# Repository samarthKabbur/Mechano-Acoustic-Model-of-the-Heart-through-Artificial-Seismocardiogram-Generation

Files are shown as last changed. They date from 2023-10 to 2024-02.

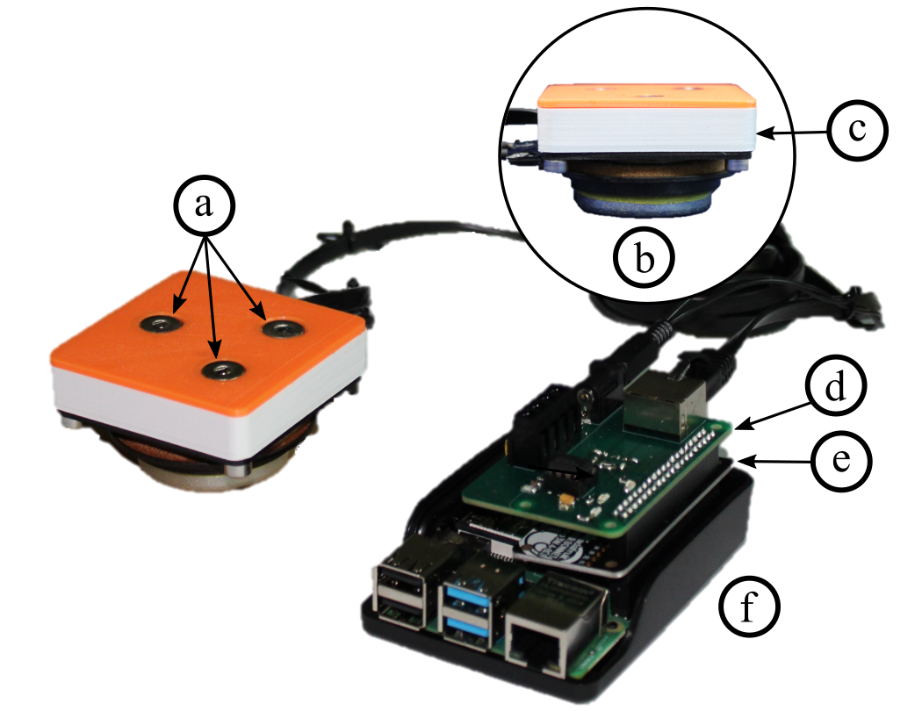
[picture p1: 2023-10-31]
SCG Generator/rPi Backups/Desktop/SyntheticSCG-Hardware-main/figures/figure1.png

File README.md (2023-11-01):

# Mechano-Acoustic-Model-of-the-Heart-through-Artificial-Seismocardiogram-Generation

URF Project Development Proposal for a Mechano Acoustic Model of the Heart through Artificial Seismocardiogram Generation and Cardiac Tissue Modeling
PI: Dr. Nanshu Lu, Mentor: Sarnab Bhattacarya, Researcher: Samarth Kabbur, University of Texas at Austin
Background and Statement of Objectives
1 			2			3		

Figure 1: Assorted imagery. 1. Heart with muscle damage and blocked artery. 2. SCG data collection flowchart. 3. Proposed artificial seismocardiogram generation system.
“Intelligence will transform our ability to monitor and detect heart disease,” says Dr. Peter Libby, a renowned cardiologist at Harvard-affiliated Brigham and Women's Hospital.1 His words encapsulate the ever-increasing importance of leveraging cutting-edge technologies to address one of the most prevalent and impactful health concerns affecting the public today – cardiac complications (Fig 1.1). 
At the forefront of cardiac monitoring is seismocardiography, or SCG, which allows us to measure the mechanical motion of the heart. SCG has shown remarkable promise in its utility, holding the potential to revolutionize the early detection and prediction of atrial fibrillation6, CAD7, and heart failure6,7, potentially years before they manifest clinically (Fig 1.2). While the promise of SCG is undeniable, the development of sensors capable of accurately measuring SCG and deriving meaningful physical characteristics of the heart from its signals has been hindered by challenges. Progress has been slow, and the cost of development has been prohibitive.2 In response to these limitations I aim to create a device that advances upon the capabilities of existing artificial SCG waveform generators.This device will have the ability to artificially generate a wide range of waveforms, enabling researchers to rigorously test their SCG sensors by placing them on top of artificial tissue. By doing so, we will establish an anatomically accurate mechano-acoustic model of the heart, enabling the development and testing of non-invasive devices under various simulated heart conditions (Fig 1.3). The implications of such a device are profound, as it can be employed broadly in research clinics and commercial testing, provided it receives the necessary approvals.
While existing SCG Generator Phantoms have demonstrated the ability to replicate SCG waveforms with up to 90% accuracy, there remain several unexplored avenues.3 This research seeks to answer important questions regarding the use of alternative transduction methods, such as piezoelectric, for SCG generation. Additionally, by introducing configurable noise and artifact simulation into the system, this study aims to enhance the utility of artificial SCG signal generation for algorithm testing.
The significance of this study will be underscored if the developed device consistently and accurately reproduces SCG waveforms recorded by gold standard SCG sensors in real human subjects. Furthermore, the incorporation of artificial tissue layers into the waveform generation process holds the potential to contribute to the creation of more realistic SCG waveforms, advancing the state of the art in this field.This research is expected to be of particular interest to seismocardiogram researchers and those involved in SCG sensor development, as it promises to accelerate the testing phase of their projects. Many within our laboratory share these research interests.
In conclusion, the objectives of this study are twofold: the primary objective is to assess if the inclusion of artificial tissue composed of PDMS and other biopolymers enhances the accuracy of artificial SCG waveforms, while the secondary objective seeks to explore the procedural combination of noise artifacts with SCG waveforms.  It addresses critical questions, introduces innovative approaches, and holds the promise of improving the reliability and accuracy of SCG sensor technology.
Proposed Research Plan
    1			2	                  3			   4

Figure 2: Prototype results of a speaker based SCG transduction/generation platform. 1. The 10.7cm x 10.7cm base plate and ADXL355 accelerometer 2. The hexagonal cross-structure and sandwich. 3. Side profile reveals the Visaton EX60-S electrodynamic exciter, printed support base, bottom cushion, and the top placement of direct SCG measurement 4. rPi 3B computational structure for interface with the exciter and accelerometer. The rPi hat is developed by Nikbakht et.al.
2.1 Build and validate a speaker based SCG transduction platform that allows for the vibrational playback of Heartsound.wav waveforms.
Under the guidance of my mentor and previous work on a SCG Generator Phantom (hardware and software) by Nikbakht et.al3 I have developed a mechano-acoustic foundation for the artificial generation of SCG waveforms, a critical component of our research methodology (Fig 2). This system has been structured to facilitate validation through external sensor measurements. The core of this setup features a carefully designed base plate characterized by dimensions and curvature tailored to minimize internal echoes (Fig 2.1). Positioned atop this base plate is an accelerometer, responsible for recording the SCG waveform (Fig 2.1). To bolster mechanical coupling and optimize vibration transmission, a hexagonal cross structure is sandwiched within (Fig 2.2). The uppermost layer comprises a thin, rigid printed plastic roof plate, serving as the platform for the placement of the external SCG measurement device (Fig 2.3). Connecting these elements is a Raspberry Pi housing Python code that not only transmits the SCG waveform for playback but also collects internal vibration data from the accelerometer (Fig 2.4).
This endeavor benefits from the existence of more advanced software, as seen in the work by Nikbakht et.al. This software encompasses a comprehensive suite of features, including a feedback transfer function for waveform calibration against noise, error handling mechanisms, terminal-based inputs for precise control over playback, and it performs well on my mechanical model. In my research, I intend to draw inspiration from and further develop this existing codebase to refine and optimize my own system for SCG signal generation and validation.
	2.2 Build and study the effect of anatomically correct cardiac tissue layers composed of eco-polydimethylsiloxane and other bio-polymers on the generation of accurate artificial seismocardiogram waveforms.
SCG sensors do not sit directly on top of the heart, rather they read signals that need to travel through many layers of bone and tissue, including the myocardium, peritoneum, sternum, etc.2 Using our available eco-PDMS and other biopolymers as necessary, I will create layers of variable thickness, density, and composition to create a low-level structure mimicking the anatomical layers of the heart. The layers will rest on the top surface of the existing SCG Generator. Experimental testing will determine if the biostructure allows for a generation of a more accurate SCG signal, compared to a barebones platform. The testing will include varying the mechanical coupling between layers, changing the weight of the sensor itself, and varying tissue density all as independent variables.
	2.3 Create an algorithm that can incorporate noise artifacts (walking, running, stomach palpitations, small impulse) into a clean SCG signal.
Available SCG databases are limited, and sometimes a researcher may want to test their sensors on a unique signal that isn’t available to us. For example, the topic of research may deal with creating an e-tattoo that can detect SCG features while the patient is walking, running, etc. Citation no. 2 also describes this problem as a gap in existing literature. I will create a novel program that can combine noise artifacts generated by walking, running, hiking, swimming, etc. with a ‘clean’ SCG signal, in order to simulate a ‘dirty’ signal. Such a signal would then be played in the SCG Generator for testing purposes, allowing the researcher to test their device on a large variety of signals, all on a small in-house machine, allowing them to minimize expensive human trials.
Project Schedule and Milestones
Task
Subtask
Y1
Q1
Q2
Q3
Q4

1
Optimize and groove mechanical structure 

Mitigate external noise

2
Methodize variable density PDMS production

Manufacture tissue layers

Validate signal accuracy

3
Accumulate noisy and clean datasets

Procedural generation of noisy signal

Validate signal accuracy to ground truth

Review of Literature
A seminal external study that significantly informs the present research is the work titled "A Synthetic Seismocardiogram and Electrocardiogram Generator Phantom," authored by Mohammad Nikbakht et. al. This study introduced a portable and innovative system designed to synthetically generate SCG and electrocardiogram (ECG) signals. The researchers developed a Raspberry Pi-based system capable of replicating input SCG and ECG waveforms as physical acceleration and voltage outputs. For SCG generation, an off-the-shelf exciter speaker was employed as a mechanical transducer, and its transfer function was meticulously calibrated to ensure accurate replication of SCG waveforms. The system's performance was rigorously validated using human SCG and ECG data, achieving a remarkable >90% correlation between input and output signals in both time and frequency domains. Importantly, amplitude errors were maintained within clinically acceptable ranges, allowing the system to produce realistic waveforms with amplitudes corresponding to critical cardiac features. This innovation enables safe data collection in environments unsafe for human participants and provides a valuable source of ground truth signals.
While the aforementioned study represents a significant advancement in SCG signal generation, there remain opportunities for further development and improvement. First, expanding the validation process to encompass more diverse SCG morphologies, as well as various cardiac conditions, will enhance the applicability and reliability of the synthetic signal generator. The addition of noise artifacts associated with walking, running, and other forms of human mobility to the input waveform can help synthesize the effect of real world continuous processes on the heart. Finally, the proposed research seeks to build upon this foundation by creating a device that not only generates SCG signals but also incorporates artificial tissue layers to model the complex physiological nuances of the human body.
Budget
Raspberry Pi 4b+ KIT: Faster processor unlocks real time SCG processing and computationally intensive Python packages: $186
PDMS and Crosslinker: Biopolymer to simulate tissue layers: $175
Visaton 60s Electrodynamic Actuator x2: Generates the main SCG signal: $160
PAD Ex 60s x4: $120 x2: Adheres generator to surface, minimizes noise: $20
Piezoelectric Actuator: To study other methods of SCG generation: $12
Foam Padding: To pad external connections to minimize noise and internal vibration: $5
Polylactic Acid Filament: 3D printer material for foundation fabrication: $19
Ninjaflex Polyurethane Filament: 3D printer material for flexible plastics $28
Florida Biomedical Society 2024 Conference. (Coronado Springs, Florida, Feb 8-11, 8:30-10pm daily session time). The FBSS contains 48 hours of education sessions on topics relating to biomechanics. Researcher has identified these learning opportunities as valuable for the progress of his project, and has identified attending individuals, companies, and products highly relevant to this research and my career goals: $189 Registration Fee + $144 Hotel Fee. The researcher agrees to cover all extra conference related fees to guarantee attendance. (https://www.cmia.org/events/florida-biomedical-society-2024-symposium/)
Total: $938
The materials in the itemized budget are essential to the design and production of the proposal and validation study. While basic lab materials and electronic elements are available through courtesy of the PI, URF funding will expedite my research progress. It will also allow for stronger validation testing, robust manufacturing of the model, and quality materials.
References Cited
1.	Can a smart watch diagnose a heart attack? Harvard Health https://www.health.harvard.edu/heart-health/can-a-smart-watch-diagnose-a-heart-attack.
2.	Taebi, A., Solar, B. E., Bomar, A. J., Sandler, R. H. & Mansy, H. A. Recent Advances in Seismocardiography. Vibration 2, 64–86 (2019). doi: 10.3390/vibration2010005.
3.	A Synthetic Seismocardiogram and Electrocardiogram Generator Phantom. doi:10.1109/SENSORS52175.2022.9967101 
4.	Blocked Artery https://www.flickr.com/photos/nihgov/33328945325.
5.	Heart beat detection algorithm flowchart. https://www.researchgate.net/figure/Heart-beat-detection-algorithm-flowchart_fig3_33661771
6. M. Pankaala et al., “Detection of atrial fibrillation with seismocardiography,” doi: 10.1109/EMBC.2016.7591695.
7. I. Korzeniowska‐Kubacka, “Usefulness of Seismocardiography,” doi: 10.1111/j.1542-474X.2005.00547.x.

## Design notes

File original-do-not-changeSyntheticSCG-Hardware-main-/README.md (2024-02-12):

# Synthetic ECG SCG Generator Hardware

The seismocardiogram (SCG) is a measure of chest wall vibrations resulting from the heartbeat. The SCG is typically
recorded using a low-noise accelerometer placed on the mid-sternum and contains features related to cardiovascular
activity such as aortic valve opening (AO) and aortic closing (AC). These features can support assessment of cardiovascular health and have been used in conjunction with other physiological signals to monitor key health parameters such as blood volume status and intracardiac filling pressures.

Electrocardiogram (ECG) signal reflects the electrical activity of the heart observed from the strategic points of the human body and represented by quasi-periodic voltage signal.
<!-- 
These signals fiducial points correspond to characteristic events in the cardiac cycle. For the SCG, the labels correspond to the physiological event they are believed to represent: MC, mitral valve closure; IVC, isovolumetric contraction; AO, aortic valve opening; RE, rapid ejection; AC, aortic valve closure; MO, mitral valve open- ing; and RF, rapid filling. -->

<!-- However, SCG signals are small signal, and they can get distorted easily by motion artifacts. Therefore exploring denoising methods is of great importance for SCG signals. Clearing out the noise enables extraction of physiologically relevant information from SCG. To study denoising methods, we need to collect SCG signals in noisy environments, but it is unsafe to use human subjects for such data collection in some high motion environments (medical transport helicopters). To address this, here we designed a phantom that can generate SCG and ECG signals synthetically. This enables us to collect data in those noisy environmnets without human subject involvement.
 -->
In this work, we introduce a portable USB-C powered Raspberry Pi-based system that can replicate any SCG and ECG signal inputs with minimal error in forms of acceleration and voltage. The SCG signals are generated using an off the shelf exciter speaker, and the ECG signals are generated using a voltage amplifier through 3 conductive pads. The generated signals can be recorded using the same wearable devices that are used to measure human SCG and ECG signals. Thus, this system can be used as a safer, more convenient alternative to human participants in high external vibration environments for testing and validating
classification/regression tasks and noise reduction algorithms.

## The Hardware 

he system proposed in this work consists of an actuator unit and a processing unit. The actuator unit, which generates SCG and ECG signals. 

<p align="center">
Image of The ECG/SCG Patch
</p>

<!-- <img src="https://github.com/mohnikbakht/Synthetic_ECG_SCG_Generator_Demo/blob/main/Images/Actuator2.png" alt="Image of The ECG/SCG Patch" width="300"/> -->

The system designed here offers two user-controlled modes of operation: (1) calibration, which re-estimates the transfer function of the exciter speaker with the added load on the platform (wearable sensors) , and (2) signal generation, which generates the ECG and SCG sequences.

A block diagram of the system operation:
<p align="center">
 Image of The ECG/SCG Patch
</p>

### Commands

1) Calibration mode: Calibrate the system (in a new environment):

calculate the transfer function of the actuator using a sine sweep and use it to calibrate the SCG beats to be ready for generation
 
```console
python3 SCG_Generator.py tf_estimate desktop
python3 SCG_Generator.py calibrate seq_synth desktop (or any file name [without .pkl])
```
<!-- 
<img src="https://github.com/mohnikbakht/Synthetic_ECG_SCG_Generator_Demo/blob/main/Images/calibrate_1.png" alt="Image of The ECG/SCG Patch" width="400"/> -->

2) Generation mode: Generate SCG waveforms:

generate SCG and ECG signals using the calibrated beats stored in the previous step

```console
python3 SCG_Generator.py generate seq_synth_calibrated desktop (or any file name you stored the calibrated signals [without .pkl])
```

<!-- <img src="https://github.com/mohnikbakht/Synthetic_ECG_SCG_Generator_Demo/blob/main/Images/generate_1.png" alt="Image of The ECG/SCG Patch" width="400"/> -->

## Use

Depending on the type of the connection to the RPi, there are 2 options:
1) If a display is connected to the RPi (or have X11 forwarding enabled), the plots will be shown in separate windows. Use this command (this mode is default):
```console
python3 SCG_generate.py generate signal_sample_calibrated desktop
```
2) If communication is through a terminal only, the plots will be plotted in the terminal (lower quality). Use this command:
```console
python3 SCG_generate.py generate signal_sample_calibrated terminal
```
## Output Recording Samples

A sample of the generator-output SCG and ECG compared to the ECG and SCG inputs:

<p align="center">
Image of The ECG/SCG Patch
</p>

Bland-Altman plots of error between the measured generator-output and the real human signal input based on the amplitude of the most prominent
feature of the beats after heartbeat segmentation for (a) SCG, and (b) ECG signals. 

<p align="center">
Image of The ECG/SCG Patch
</p>

<!-- Zoomed in:

<img src="https://github.com/mohnikbakht/Synthetic_ECG_SCG_Generator_Demo/blob/main/Images/sample_2.png" alt="Image of The ECG/SCG Patch" width="600"/>

 -->

## Reference

Please cite this paper:

M. Nikbakht, D. J. Lin, A. H. Gazi, and O. T. Inan, “A synthetic
seismocardiogram and electrocardiogram generator phantom,” in 2022
IEEE Sensors, in press.

BibTeX format: 

@inproceedings{nikbakht2022synthetic,
title={A Synthetic Seismocardiogram and Electrocardiogram Generator Phantom},
author={Nikbakht, Mohammad, and Lin, David J., and Gazi, Asim H., and Inan, Omer T.},
note={in press},
booktitle={2022 IEEE Sensors},
% pages={Accepted},
% year={2022},
% organization={IEEE}
}

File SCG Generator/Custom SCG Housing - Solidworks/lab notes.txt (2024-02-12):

propyl alchohol destroys polycarbonate plastics and filmms

methyl alchohol destroys ABS plastics and films : is polycarbonate film elastic

sent two to pig, and one broke. pig study was good data, then went bad. pig people gave singular ppg waveform so it was useless bc spO2 was needed.
btw in the interest of good communication, here's everything im working on and an approximate time frame:

projects:vibration table using raspberry pi
	
	 soluble plastic film for easier recycling of chest e-tattoo.

to learn:

	raspberry pi interface
	C code
	python signal processing MIT BSC lab
	ML algorithms
	Embedded systems
	LHR application
	IEEE robotics application
	matlab
	fast fourier transform
	signal filtering and the different types of filter implementation like Butterworth, chevychev etc. And how to filter signals based 	on set frequencies

to talk to:
	
	talk to tiande for the ecg tattoo codebase. he comes in around 4:30pm.
	talk to jishnu for sneaking into embedded systems lab
	-> the chemicals lady in the soft bioelectronics lab for getting plastics, alchohols, and training on the fume hood.

meetings:
	team meeting - tuesday at 3pm
	group meeting - friday at 9am

to organize: 
	CAD/Eagle model of chest e-tattoo
	calendar
	github codebase
	research/notes of raspberry pi 

possible projects: 
	fully flexible ears
	higher wire density
	SpO2 on the chest
	moving from coin cell to lion battery 
	trimodal: PPG, SCG, ECG
	bimodal: SCG, ECG
	dual device: SCG+SCG, ECG

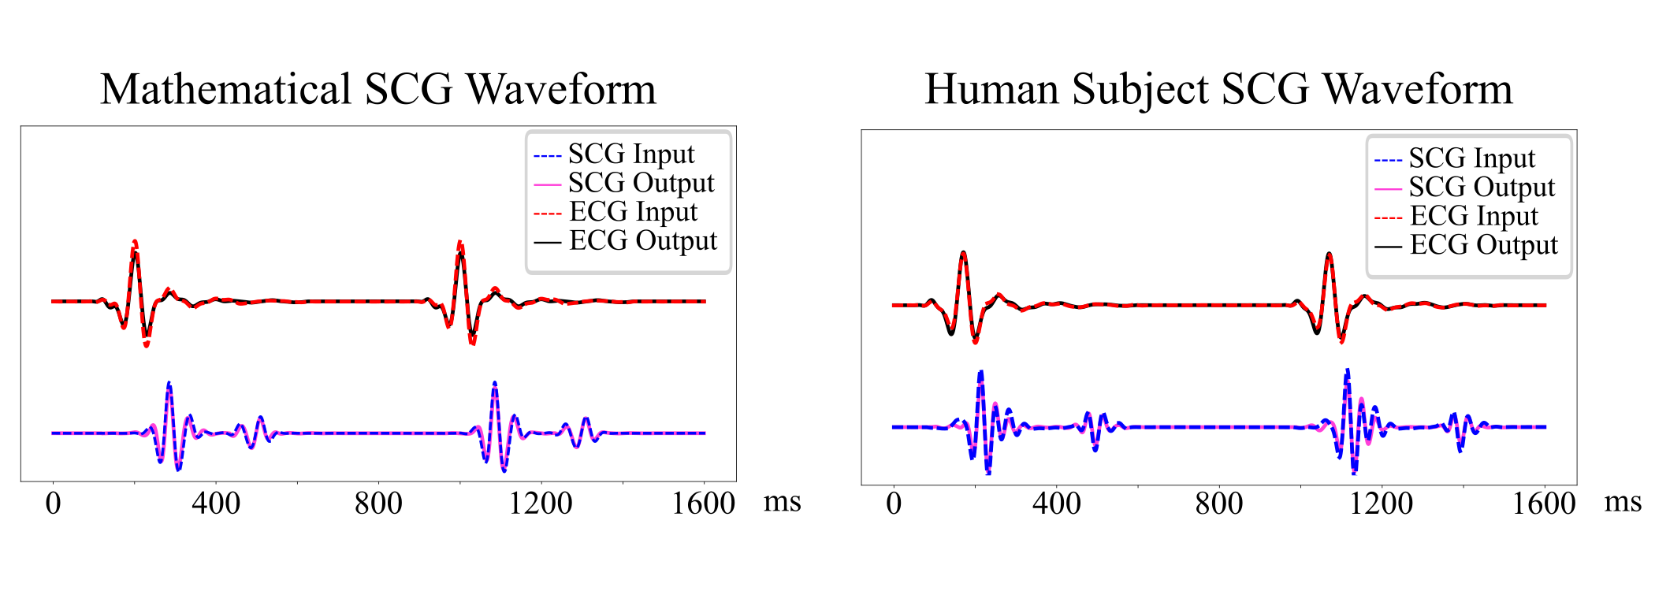
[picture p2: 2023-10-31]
SCG Generator/rPi Backups/Desktop/SyntheticSCG-Hardware-main/figures/figure3.png

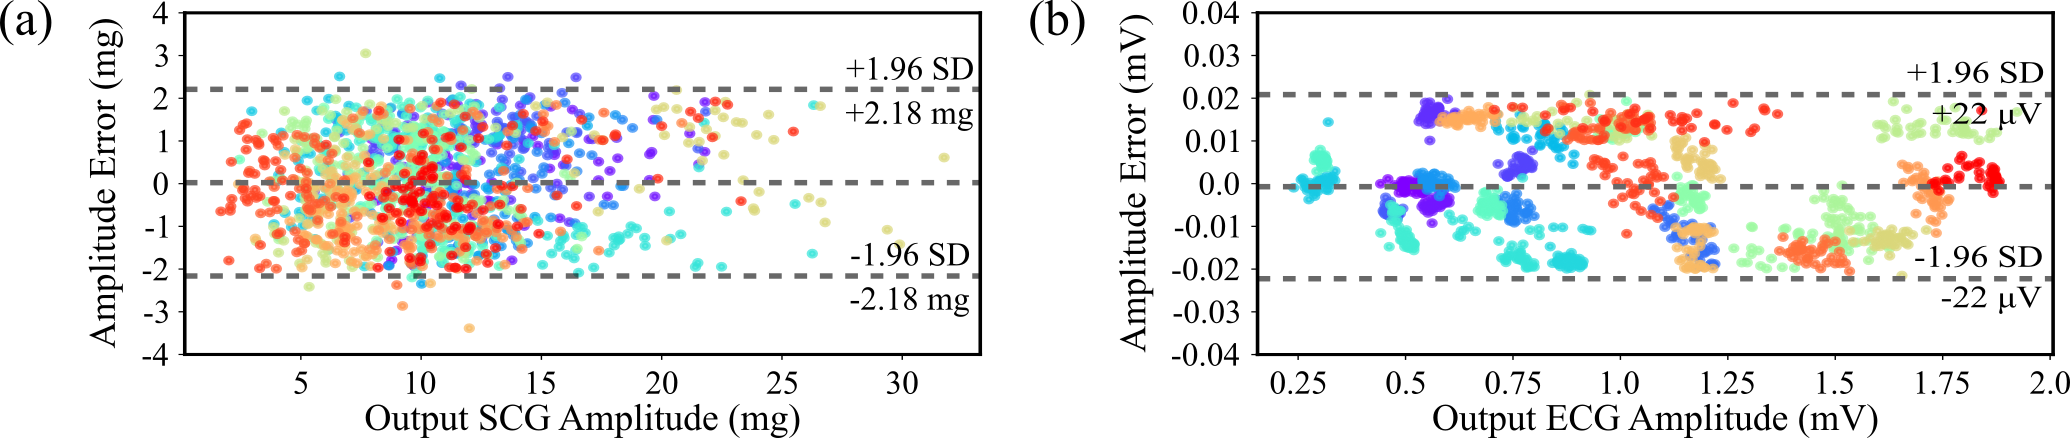
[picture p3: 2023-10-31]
SCG Generator/rPi Backups/Desktop/SyntheticSCG-Hardware-main/figures/bland-altman.png

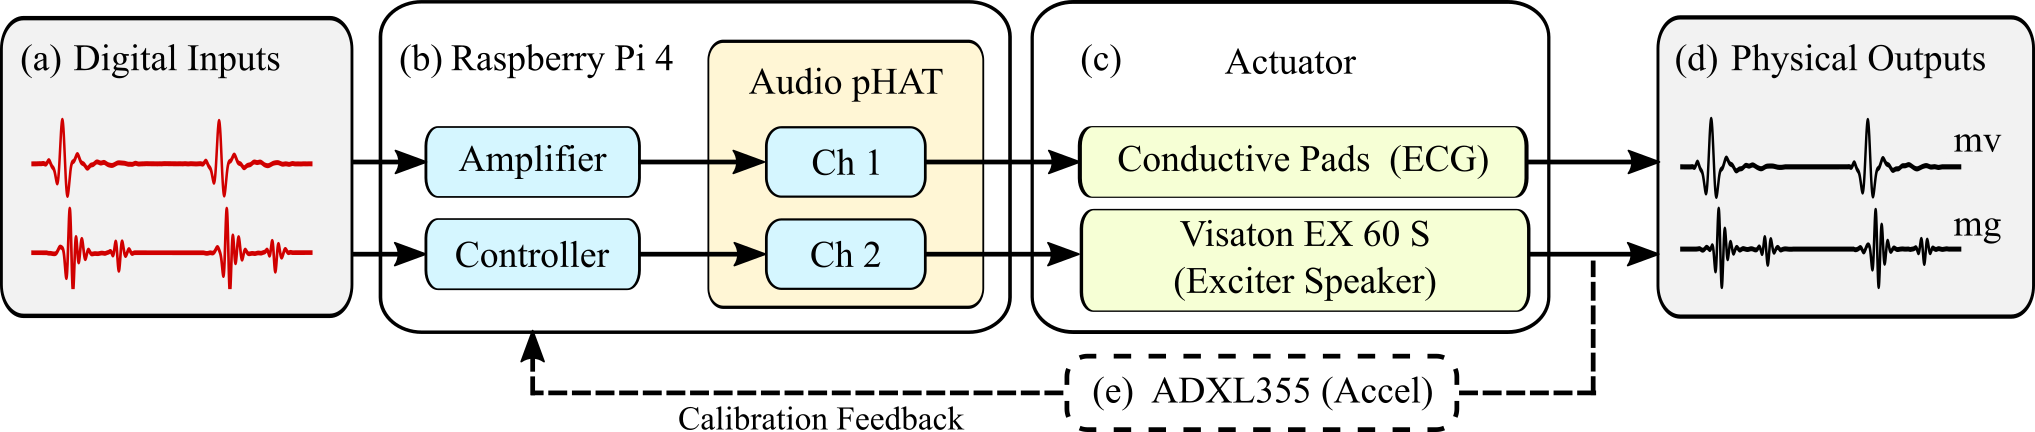
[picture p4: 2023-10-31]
SCG Generator/rPi Backups/Desktop/SyntheticSCG-Hardware-main/figures/figure2.png

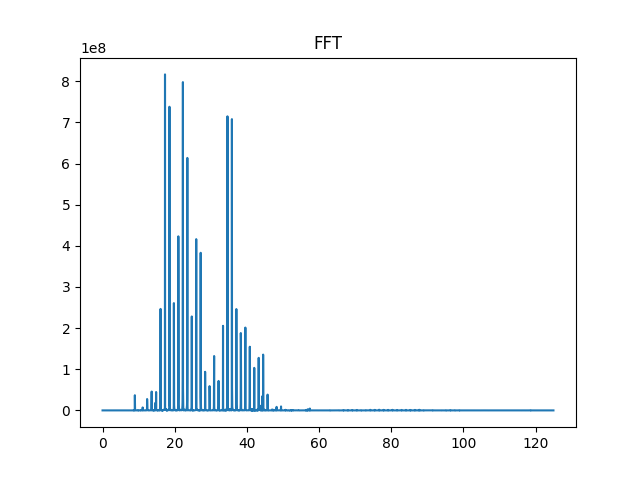
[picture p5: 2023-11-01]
oldbase-RPi code/Trials/Trial 2/fft.png

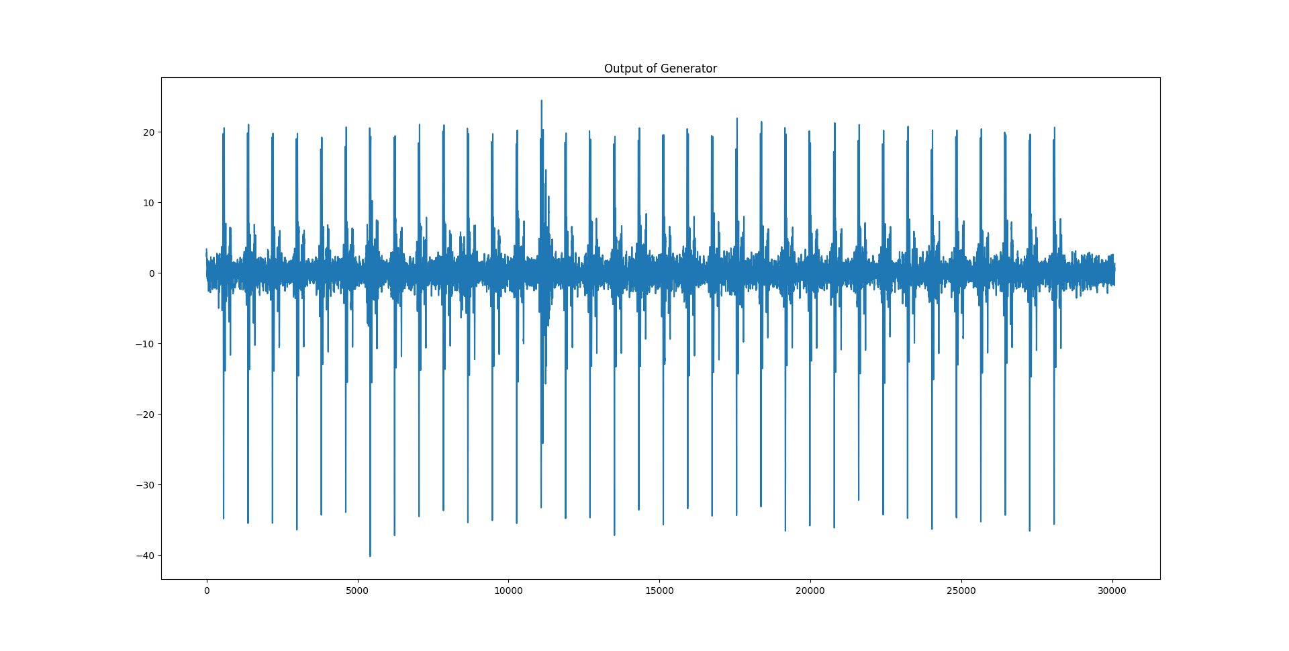
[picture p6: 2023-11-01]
oldbase-RPi code/Trials/Trial 1/Figure_1.png

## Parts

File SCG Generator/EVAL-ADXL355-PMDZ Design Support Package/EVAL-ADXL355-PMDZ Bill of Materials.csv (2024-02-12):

TITLE: Bill of Materials
BOM NO: 05_043217-b.csv
DATE: 01/24/2017
DESIGN: 02_043217b_top
TEMPLATE: Z:\allegro\v166_site\cdssetup\template.bom
CALLOUT:
ITEM# | Qty | WW_PN | DESCRIPTION | VALUE | JEDEC_TYPE | TOL | VOLTAGE | WATTAGE | LOCATION | MFG | MFG_PN | HLM_STATUS | STOCKROOM_WL | STOCKROOM_GT | STOCKROOM_LK | STOCKROOM_GBO | STOCKROOM_NSH | CUSTOM_PART | DNI
1 | 1 | 08_043217b | PCB | ? | ? | ? | ? | ? | ? | Analog Devices Supplied | 08_043217b | N/A | ? | ? | ? | ? | ? | ? | ?
2 | 4 | E022221 | CAP CER MULTILAYER X7R | 0.1uF | C0603 | 5 | 16V | N/A | C1,C2,C4,C5 | KEMET | C0603C104J4RACTU | REL | N/A | N/A | N/A | N/A | N/A | ? | ?
3 | 2 | E020723 | CAP CER X5R | 10uF | C0603 | 10 | 10V | N/A | C3,C6 | TDK | C1608X5R1A106K080AC | REL | N/A | N/A | N/A | N/A | N/A | ? | ?
4 | 1 | E015984 | IND CHIP FERRITE BEAD | 330OHM | L0603 | 25 | N/A | N/A | E1 | MURATA MANUFACTURING | BLM18SG331TN1D | REL | N/A | N/A | N/A | N/A | 7005146 | ? | ?
5 | 1 | E002359 | INDUCTOR FERRITE BD | 39OHM | L0805 | N/A | N/A | N/A | E2 | PANASONIC | EXC-ML20A390U | REL | A048-0002-010 | N/A | N/A | 1424_CAB3 | 7005175 | ? | ?
6 | 1 | E018495 | CONN-PCB HDR RA CUSTOMIZED PIN NUMBERING -PMOD | TSW-106-25-F-D-RA | CNHDRRA2X6H240 | N/A | N/A | N/A | P1 | SAMTEC INC | TSW-106-25-F-D-RA | NON-PREF | N/A | N/A | N/A | N/A | N/A | ? | ?
7 | 1 | E025232 | RES THICK FILM CHIP JUMPER, GENERAL PURPOSE | 0 | R0402 | N/A | N/A | 1/16W | R1 | YAGEO | RC0402JR-070RL | REL | N/A | N/A | N/A | N/A | 7008627 | ? | ?
8 | 1 | E024010 | IC-ADI LOW NOISE, HIGH STABILITY, LOW POWER 3AXIS ACCELEROMETER, PRELIM | ADXL355BEZ | LCC14_A | N/A | N/A | ? | U1 | ADI | ADXL355BEZ | RWC | N/A | N/A | N/A | N/A | N/A | ? | ?
The following components are part of the PCB or are NOT to be installed
ITEM# | Qty | WW_PN | DESCRIPTION | VALUE | JEDEC_TYPE | TOL | VOLTAGE | WATTAGE | LOCATION | MFG | MFG_PN | HLM_STATUS | STOCKROOM_WL | STOCKROOM_GT | STOCKROOM_LK | STOCKROOM_GBO | STOCKROOM_NSH | CUSTOM_PART | DNI

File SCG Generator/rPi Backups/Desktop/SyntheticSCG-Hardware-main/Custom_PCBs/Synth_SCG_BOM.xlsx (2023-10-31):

Part | Value | Device | Package | DigiKey Part Number
C1 | 220pF | C-US_CHIP-1206(3216-METRIC) | CAPC3216X135
C2 | 80nF | C-US_CHIP-0805(2012-METRIC) | CAPC2012X110
C3 | 220pF | C-US_CHIP-1206(3216-METRIC) | CAPC3216X135
C4 | 100nF | C-US_CHIP-0603(1608-METRIC) | CAPC1608X85
C5 | 80nF | C-US_CHIP-0805(2012-METRIC) | CAPC2012X110
C6 | 10uF | C_TANTALUM-1206(3216-METRIC) | CAPM3216X180
J1 | 1734795-1 | 1734795-1 | TE_1734795-1 | A121573-ND
J2 | PJ-035DH | PJ-035DH | CUI_PJ-035DH | CP-017DH-ND
LED1 |  | LEDCHIPLED_1206 | CHIPLED_1206
LED2 |  | LEDCHIPLED_1206 | CHIPLED_1206
LED3 |  | LEDCHIPLED_1206 | CHIPLED_1206
R1 | 10k | R-US_R0603 | R0603
R2 | 10k | R-US_R0603 | R0603
R3 | 0 | R-US_R0603 | R0603
R4 | 0 | R-US_R0603 | R0603
R5 | 4.7k | R-US_R0603 | R0603
R6 | 100R | R-US_R0603 | R0603
R7 | 100R | R-US_R0603 | R0603
R8 | NC | R-US_R0603 | R0603
R9 | 10 | R-US_R0603 | R0603
R10 | 100k | R-US_R0603 | R0603
R11 | 10k | R-US_R0603 | R0603
R12 | 100k | R-US_R0603 | R0603
R13 | NC | R-US_R0603 | R0603
RPI1 | RASPBERRYPI_BPLUS_BONNETNODIM | I2S 3W STEREO SPEAKER AMP BONNET | I2S 3W STEREO SPEAKER AMP BONNET | 1528-1819-ND
U$1 | TLV4112 | TLV4112 | DIP794W45P254L959H508Q8 | 296-10719-5-ND
U$2 | 2828XX-4282837-4 | 2828XX-4282837-4 | TERMBLK_508-4N | 281-1437-ND
 | Extra parts (digikey): |  | count
 | 2x20 Socket Riser Header for Rpi | 1528-2831-ND | 2
 | RPI female header | 1528-1785-ND | 2
 | RPi connector | 1568-1675-ND | 2
 | RPi stacking header | 1528-1385-ND
 | 12 Position Header Connector 0.100" (2.54mm) Through Hole, Right Angle | S5559-ND | 2
 | DC plug 3.5 | EP505B-ND | 2
 | Terminal blocks | ED2611-ND | 2
 | Terminal blocks | A97986-ND | 2
 | Dip socket | ED3044-5-ND | 2
 | Raspberry Pi 4 8GB | 2648-RASPBERRYPI4MODELB8G-ND | 1
 | ADXL355 eval board | 505-EVAL-ADXL355-PMDZ-ND | 1
 | ECG electrode pads | 1568-1803-ND | 2
 | Visaton EX 60 S Exciter Speaker | 2056-EX60S-8OHM-ND
 | screw and bolt 4mm
 | super glue + electric tape
 | Extra parts (Amazon):
 | Ethernet cable | https://www.amazon.com/Ethernet-Cable-1000Mbps-Universal-Computer/dp/B07H25B2S7
 | micro-SD card 32GB or 64GB

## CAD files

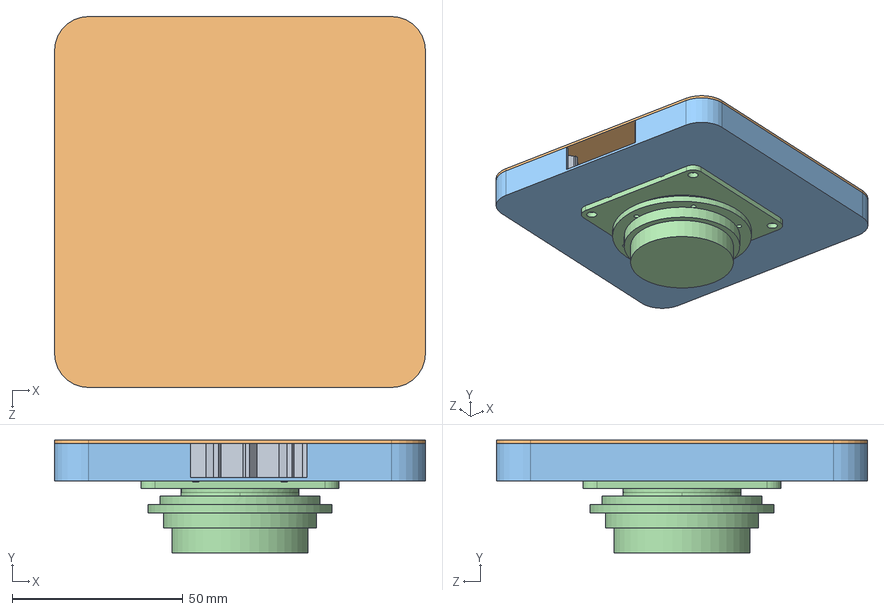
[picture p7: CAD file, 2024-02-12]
SCG Generator/Custom SCG Housing - Solidworks/speaker and attachment assembly.SLDASM
108.8 x 33.1 x 108.8 mm
visaton ex 60 s
attachment
lid
honeycomb

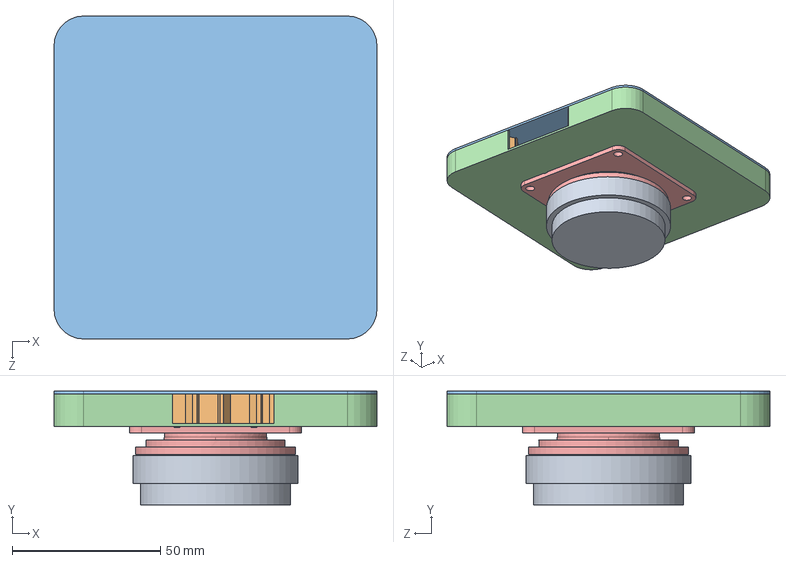
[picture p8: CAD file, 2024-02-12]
SCG Generator/Custom SCG Housing - Solidworks/speaker and attachment with BAE.SLDASM
108.8 x 38.4 x 108.8 mm
visaton ex 60 s
attachment
lid
honeycomb
visaton ex 60 s BASE

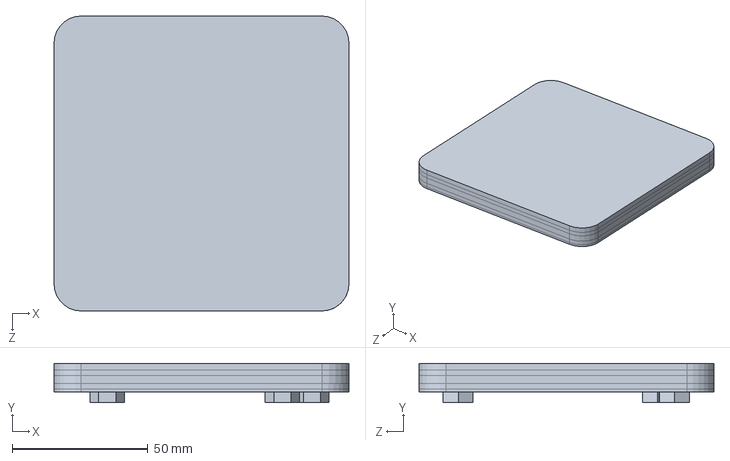
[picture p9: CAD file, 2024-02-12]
SCG Generator/Custom SCG Housing - Solidworks/lid_with_tissue_layers.SLDPRT
108.8 x 14.5 x 108.8 mm

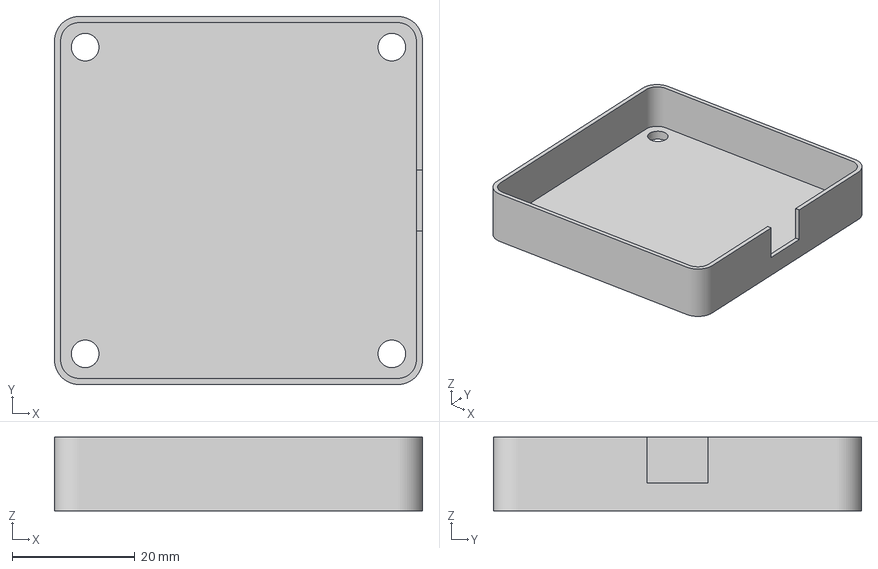
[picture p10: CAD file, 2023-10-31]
SCG Generator/rPi Backups/Desktop/SyntheticSCG-Hardware-main/Actuator_Housing_CAD_designs/Body.3mf
60.0 x 60.0 x 12.0 mm

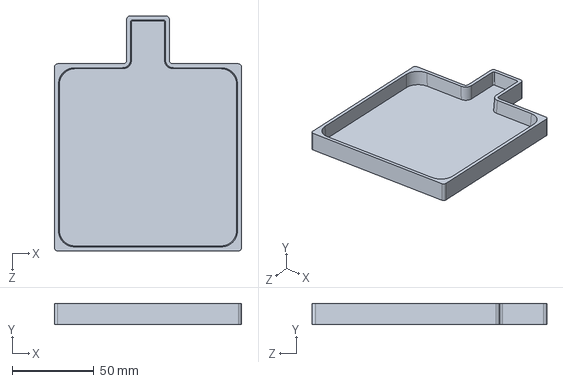
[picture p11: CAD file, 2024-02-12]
SCG Generator/Tissue Molds/mold1withlip.SLDPRT
114.8 x 13.0 x 144.1 mm

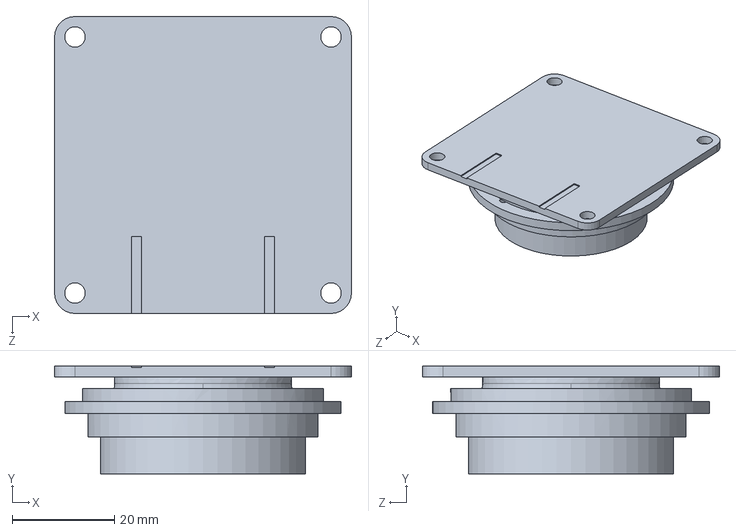
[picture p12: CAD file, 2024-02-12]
SCG Generator/Custom SCG Housing - Solidworks/visaton ex 60 s.SLDPRT
58.0 x 21.1 x 58.0 mm

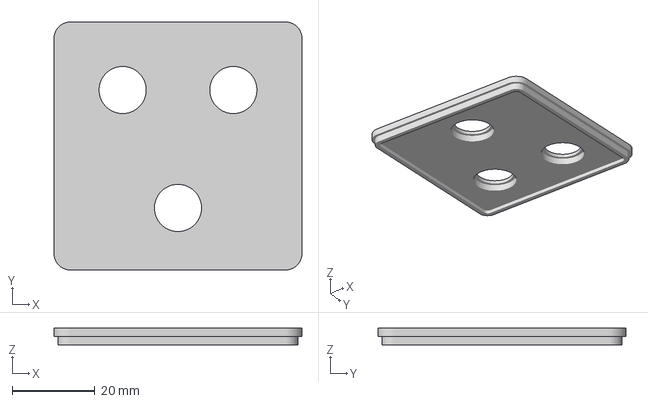
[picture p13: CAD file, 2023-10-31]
SCG Generator/rPi Backups/Desktop/SyntheticSCG-Hardware-main/Actuator_Housing_CAD_designs/Lid.3mf
60.0 x 60.0 x 4.00 mm

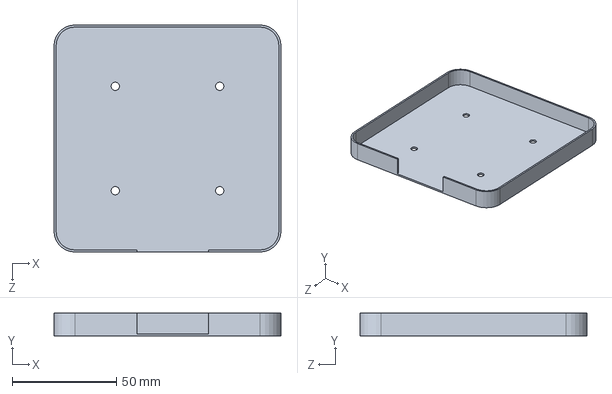
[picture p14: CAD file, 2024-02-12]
SCG Generator/Custom SCG Housing - Solidworks/attachment.SLDPRT
108.8 x 11.0 x 108.8 mm

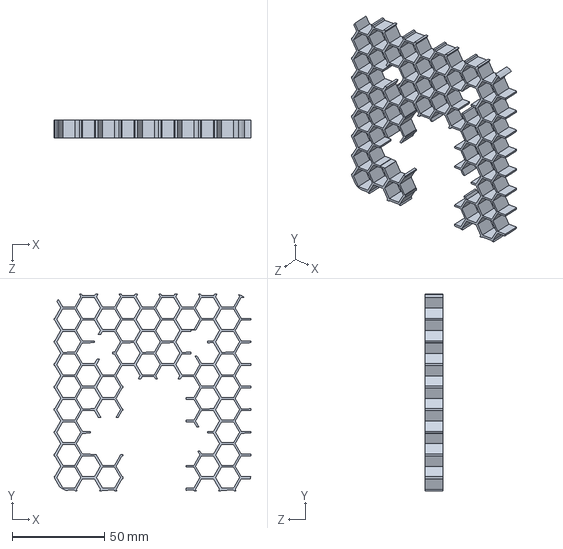
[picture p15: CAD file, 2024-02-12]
SCG Generator/Custom SCG Housing - Solidworks/honeycomb.SLDPRT
106.8 x 106.8 x 10.0 mm

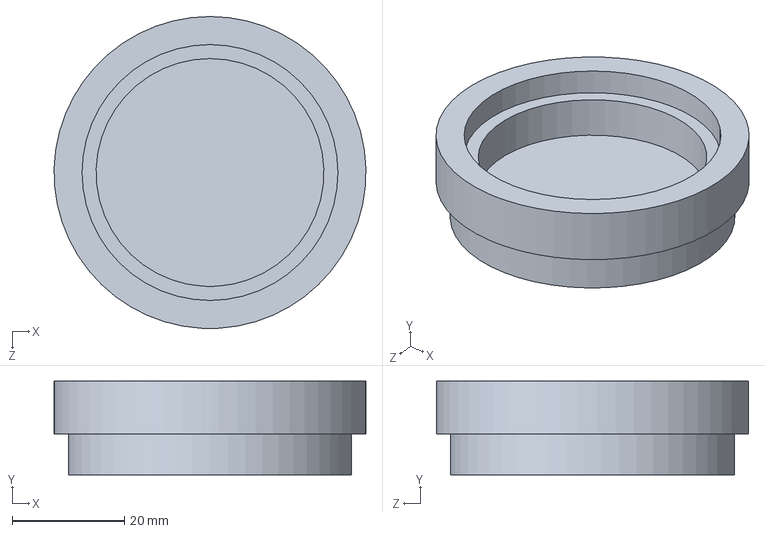
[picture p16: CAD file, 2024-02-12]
SCG Generator/Custom SCG Housing - Solidworks/visaton ex 60 s BASE.SLDPRT
55.6 x 16.7 x 55.6 mm

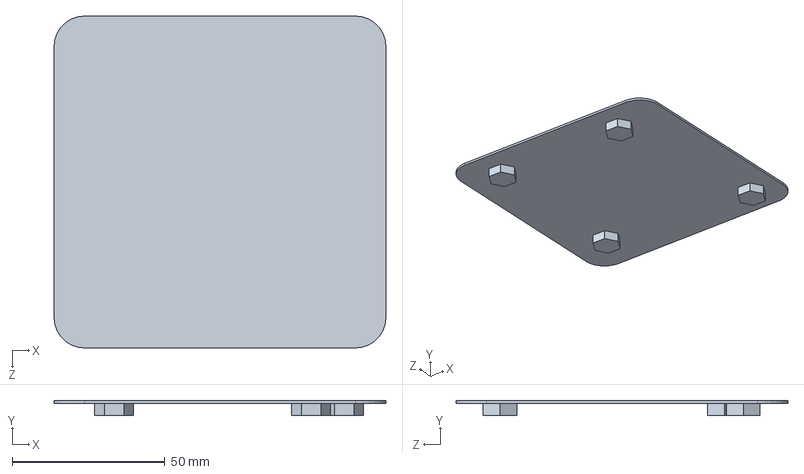
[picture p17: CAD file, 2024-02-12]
SCG Generator/Custom SCG Housing - Solidworks/lid.SLDPRT
108.8 x 5.00 x 108.8 mm

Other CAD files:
SCG Generator/rPi Backups/Desktop/SyntheticSCG-Hardware-main/Actuator_Housing_CAD_designs/Synthetic_SCG_Actuator_Housing.f3d
SCG Generator/rPi Backups/old transfer/Desktop/SyntheticSCG-Hardware-main/Actuator_Housing_CAD_designs/Synthetic_SCG_Actuator_Housing.f3d

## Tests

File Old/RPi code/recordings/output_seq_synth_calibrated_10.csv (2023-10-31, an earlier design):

-1.813951737450452129e-01
1.285004826254976251e+00
7.858048262548891216e-01
6.220048262549653373e-01
-4.879517374502029270e-02
6.454048262548894854e-01
9.496048262549265928e-01
3.568048262549154970e-01
2.710048262549662468e-01
4.036048262548774801e-01
4.738048262548772982e-01
6.142048262548769344e-01
1.316204826254875115e+00
9.160482625497934350e-02
-6.415951737450313885e-01
-5.479951737451074223e-01
4.480482625490367354e-02
-2.359951737450955989e-01
1.051004826254938962e+00
1.004204826254976979e+00
1.097804826254900945e+00
3.256048262549029459e-01
7.600482625491622457e-02
6.040482625496679248e-02
-6.415951737450313885e-01
-1.671195173745104512e+00
-1.070595173745118700e+00
5.206048262549529682e-01
2.751404826254884028e+00
4.701404826254929503e+00
4.795004826254967156e+00
1.948004826254873478e+00
7.600482625491622457e-02
-1.267951737451085137e-01
-8.521951737450308428e-01
9.184048262549140418e-01
5.596048262549402352e-01
2.236604826254961154e+00
1.940204826254898762e+00
3.022048262549787978e-01
-5.167951737450948713e-01
-2.047951737450830478e-01
1.696048262549538777e-01
6.532048262549778883e-01
4.738048262548772982e-01
-1.891951737450199289e-01
-7.819951737450310247e-01
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

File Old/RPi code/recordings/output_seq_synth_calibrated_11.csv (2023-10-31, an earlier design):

-2.439353378378427806e+00
-4.269533783783572289e-01
1.328046621621638224e+00
2.381046621621635495e+00
3.140466216216282191e-01
-1.191353378378380512e+00
-1.916753378378416528e+00
-1.557953378378442721e+00
-1.300553378378367597e+00
-6.531533783784198022e-01
-4.475337837834558741e-02
1.086246621621626218e+00
2.576046621621571830e+00
2.115846621621585655e+00
1.694646621621586746e+00
2.438466216216284010e-01
-9.885533783783557737e-01
-6.815337837838342239e-02
9.848466216216138491e-01
9.224466216215887471e-01
-3.695337837837087136e-02
-3.099533783783954277e-01
-7.595337837835813843e-02
-7.779533783783563194e-01
-9.935337837839597341e-02
-1.183553378378405796e+00
-5.829533783784199841e-01
2.906466216215903842e-01
1.624446621621586928e+00
1.975446621621586019e+00
7.976466216216522298e-01
-7.389533783783690524e-01
-1.752953378378379057e+00
-2.517353378378402340e+00
-8.793533783783686886e-01
5.948466216216274915e-01
1.671246621621548911e+00
2.201646621621648592e+00
1.008246621621651684e+00
1.554246621621587110e+00
2.092446621621547820e+00
1.437246621621625309e+00
9.846621621591111762e-03
-1.305533783784085244e-01
3.296466216215776512e-01
7.118466216215892928e-01
5.246466216216276734e-01
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

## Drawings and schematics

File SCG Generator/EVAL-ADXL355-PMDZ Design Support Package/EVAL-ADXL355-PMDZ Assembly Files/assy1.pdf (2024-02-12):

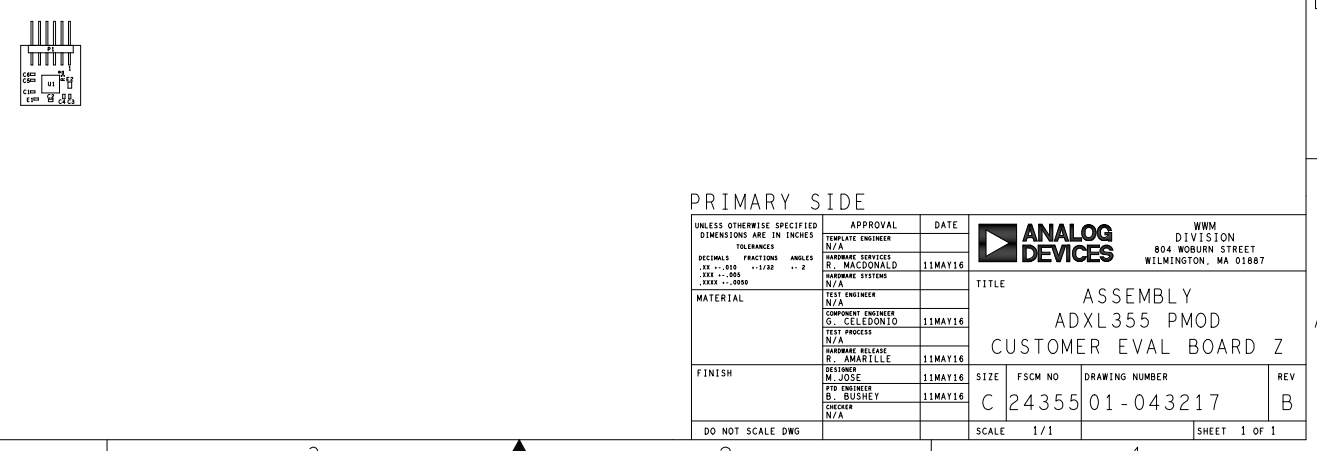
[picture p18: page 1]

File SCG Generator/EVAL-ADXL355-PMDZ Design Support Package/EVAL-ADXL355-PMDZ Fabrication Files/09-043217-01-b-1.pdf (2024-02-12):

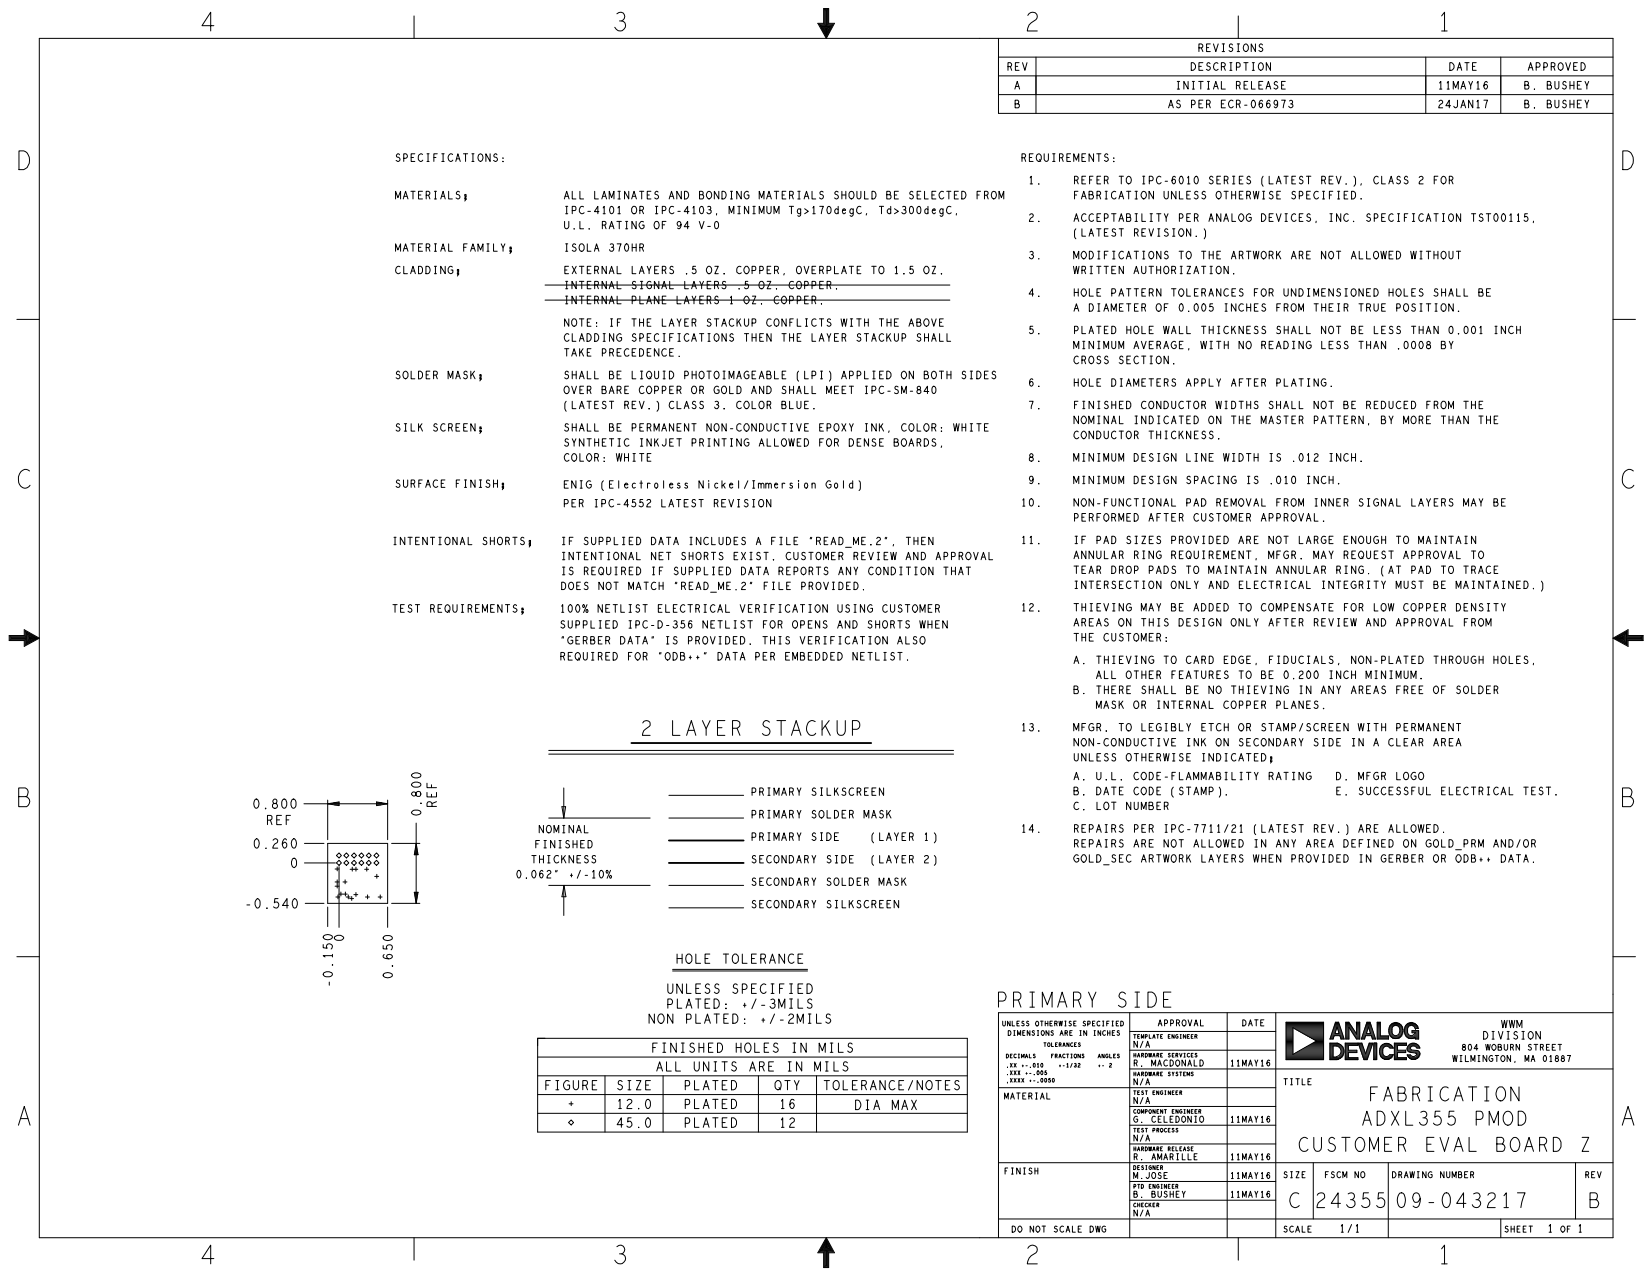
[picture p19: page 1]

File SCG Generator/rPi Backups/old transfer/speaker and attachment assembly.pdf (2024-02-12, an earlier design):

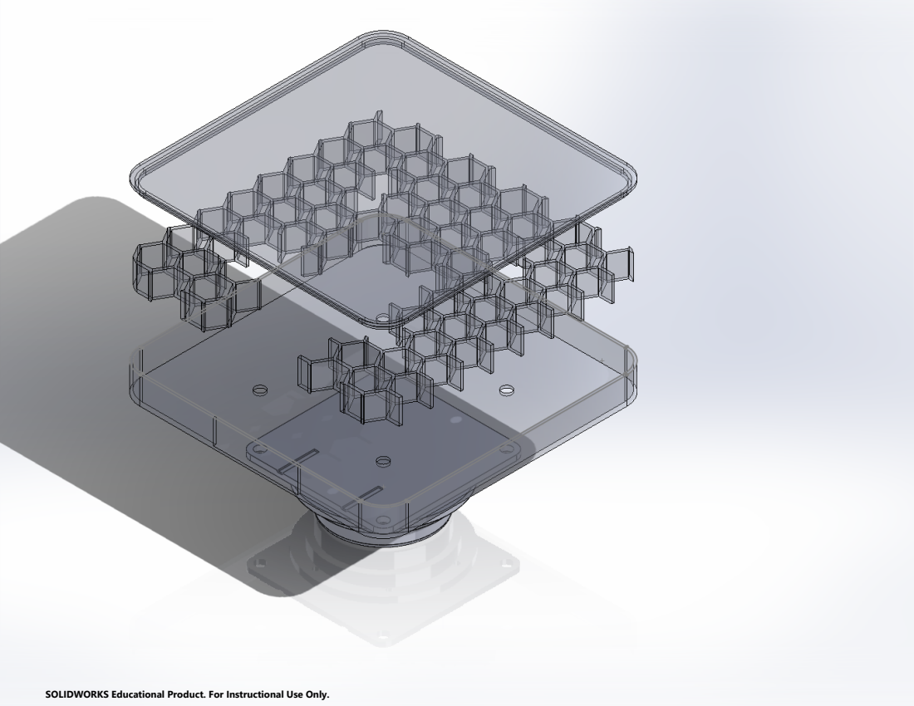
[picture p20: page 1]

SOLIDWORKS Educational Product. For Instructional Use Only.

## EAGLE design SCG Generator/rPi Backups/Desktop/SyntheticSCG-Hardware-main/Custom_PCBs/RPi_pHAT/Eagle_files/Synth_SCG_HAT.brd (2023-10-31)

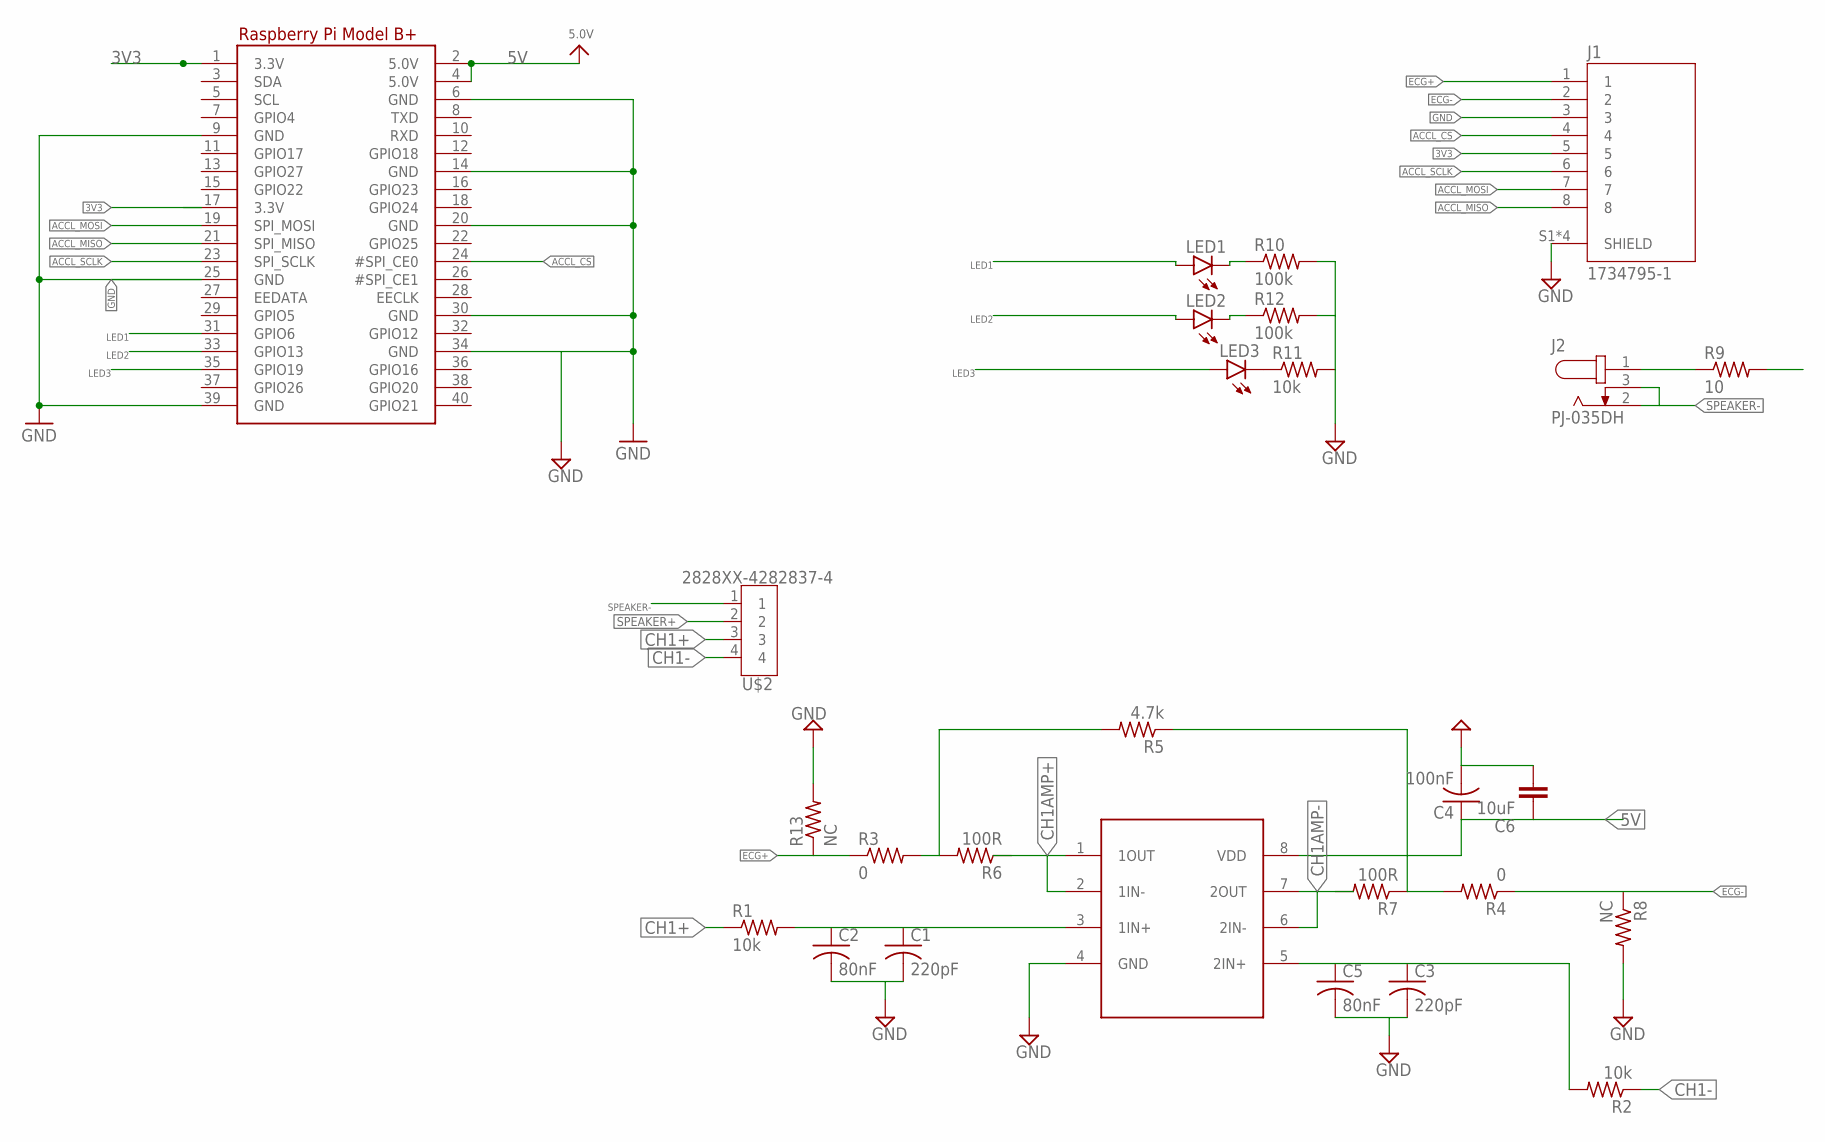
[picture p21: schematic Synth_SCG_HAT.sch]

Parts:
C1, C3: 220pF; CAPC3216X135
C2, C5: 80nF; CAPC2012X110
C4: 100nF; CAPC1608X85
C6: 10uF; CAPM3216X180
J1: 1734795-1; TE_1734795-1
J2: PJ-035DH; CUI_PJ-035DH
LED1, LED2, LED3: LEDCHIPLED_1206; CHIPLED_1206
R1, R2, R11: 10k; R0603
R3, R4: 0; R0603
R5: 4.7k; R0603
R6, R7: 100R; R0603
R8, R13: NC; R0603
R9: 10; R0603
R10, R12: 100k; R0603
RPI1: RASPBERRYPI_BPLUS_BONNETNODIM; PI_BONNET_NODIM
U$1: TLV4112; DIP794W45P254L959H508Q8
U$2: 2828XX-4282837-4; TERMBLK_508-4N

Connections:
3.3V@1: RPI1.17 (3.3V)
3V3: J1.5, RPI1.1 (3.3V)
5V: C4.1, C6.1, RPI1.2 (5.0V), RPI1.4 (5.0V), U$1.8 (VDD)
ACCL_CS: J1.4, RPI1.24 (#SPI_CE0)
ACCL_MISO: J1.8, RPI1.21 (SPI_MISO)
ACCL_MOSI: J1.7, RPI1.19 (SPI_MOSI)
ACCL_SCLK: J1.6, RPI1.23 (SPI_SCLK)
CH1+: R1.1, U$2.3
CH1-: R2.1, U$2.4
CH1AMP+: R6.1, U$1.1 (1OUT), U$1.2 (1IN-)
CH1AMP-: R7.2, U$1.6 (2IN-), U$1.7 (2OUT)
ECG+: J1.1, R3.1, R13.1
ECG-: J1.2, R4.1, R8.1
GND: C1.2, C2.2, C3.2, C4.2, C5.2, C6.2, J1.3, J1.S1 (SHIELD), J1.S2 (SHIELD), J1.S3 (SHIELD), J1.S4 (SHIELD), R8.2, R10.2, R11.2, R12.2, R13.2, RPI1.6 (GND), RPI1.9 (GND), RPI1.14 (GND), RPI1.20 (GND), RPI1.25 (GND), RPI1.30 (GND), RPI1.34 (GND), RPI1.39 (GND), U$1.4 (GND)
LED1: LED1.A, RPI1.31 (GPIO6)
LED2: LED2.A, RPI1.33 (GPIO13)
LED3: LED3.A, RPI1.35 (GPIO19)
unnamed: C1.1, C2.1, R1.2, U$1.3 (1IN+)
unnamed: R3.2, R5.2, R6.2
unnamed: C3.1, C5.1, R2.2, U$1.5 (2IN+)
unnamed: J2.1, R9.1
unnamed: R4.2, R5.1, R7.1
unnamed: LED3.C, R11.1
unnamed: LED2.C, R12.1
unnamed: LED1.C, R10.1
SPEAKER+: R9.2, U$2.2
SPEAKER-: J2.2, J2.3, U$2.1

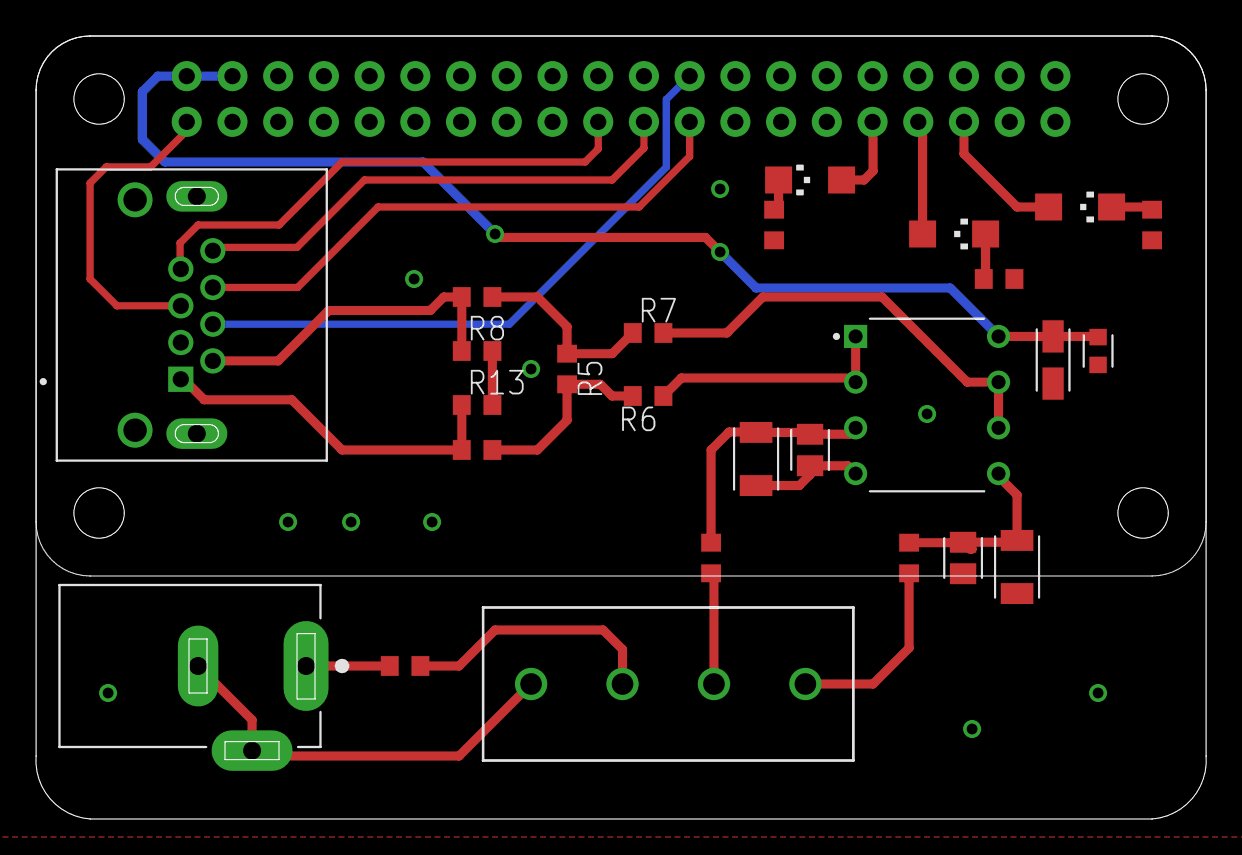
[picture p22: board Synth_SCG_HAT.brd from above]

Board: 2 copper layers, 65.0 x 43.5 mm, 27 parts (0 on the bottom side), 26 nets.

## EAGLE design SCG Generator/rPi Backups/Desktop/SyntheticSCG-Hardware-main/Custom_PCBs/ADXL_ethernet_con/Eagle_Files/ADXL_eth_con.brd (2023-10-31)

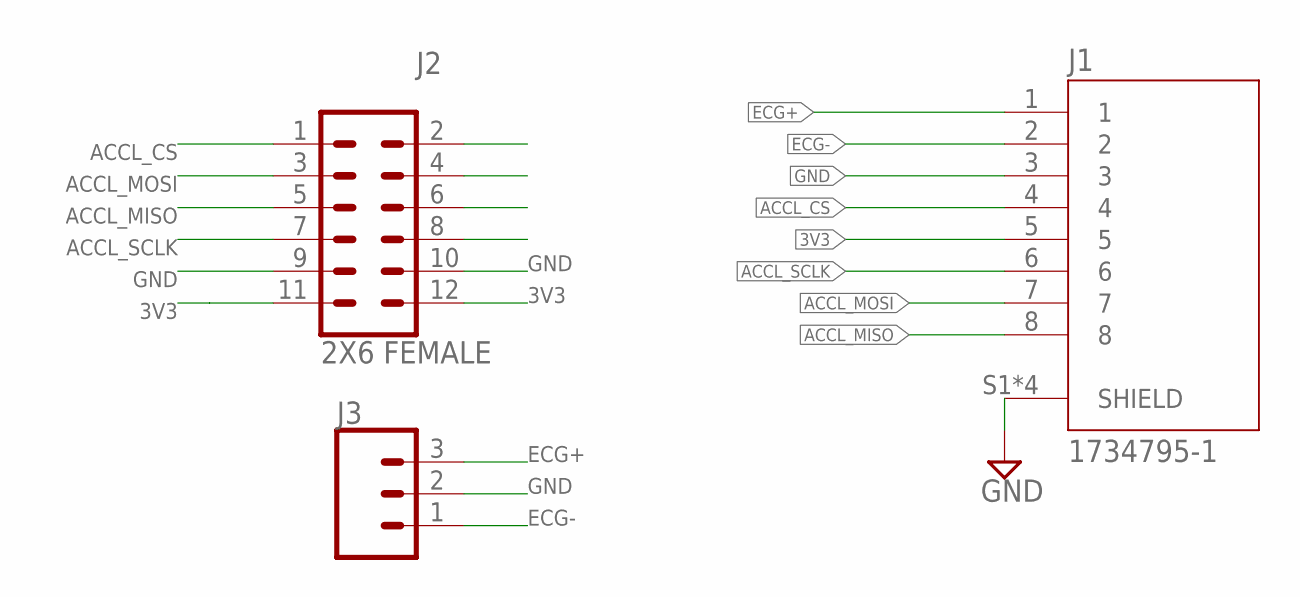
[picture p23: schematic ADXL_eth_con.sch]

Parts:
J1: 1734795-1; TE_1734795-1
J2: 2X6 FEMALE; 2X6
J3: CONN_03; 1X03

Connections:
3V3: J1.5, J2.11, J2.12
ACCL_CS: J1.4, J2.1
ACCL_MISO: J1.8, J2.5
ACCL_MOSI: J1.7, J2.3
ACCL_SCLK: J1.6, J2.7
ECG+: J1.1, J3.3
ECG-: J1.2, J3.1
GND: J1.3, J1.S1 (SHIELD), J1.S2 (SHIELD), J1.S3 (SHIELD), J1.S4 (SHIELD), J2.9, J2.10, J3.2

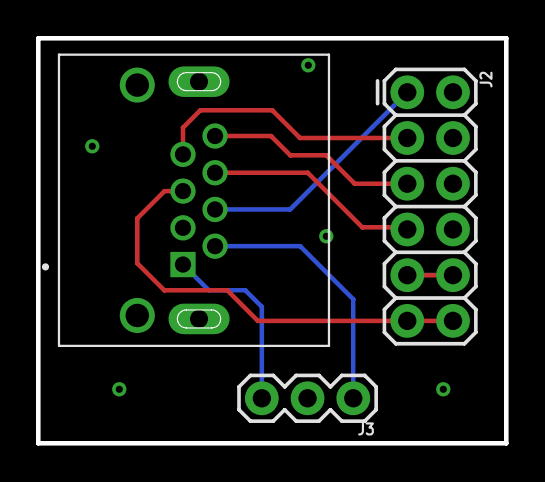
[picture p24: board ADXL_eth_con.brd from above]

Board: 2 copper layers, 26.0 x 22.5 mm, 3 parts (0 on the bottom side), 8 nets.

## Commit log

2023-10-31 unchanged RPi code + old code and waves
    [ADXL_eth_con.brd, ADXL_eth_con.sch, Body.3mf, Lid.3mf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]
2023-10-31 updated directories
    [ADXL_eth_con.brd, ADXL_eth_con.sch, Body.3mf, Lid.3mf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]
2023-11-01 new tf, calibration, generation on oldbase
    [output_seq_synth_calibrated_0.csv, output_seq_synth_calibrated_23.csv, output_seq_synth_calibrated_24.csv, output_seq_synth_calibrated_25.csv]
2023-11-01 tested old and new base. added plots
    [output_seq_synth_calibrated_0.csv, output_seq_synth_calibrated_1_0.csv, output_seq_synth_calibrated_dualadhesivebase_0.csv]
2024-02-12 adding scg generator folder
    [ADXL_eth_con.brd, ADXL_eth_con.sch, Synth_SCG_HAT.brd, Synth_SCG_HAT.sch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]
2024-02-12 added SCG generator folder
    contains adxl 355 to ethernet info, custon scg housing solidworks files, adxl 355 pinout info, phonocardiogram playback under procedural scg generation, rpi sd card backup, mohammad's OG code, and ti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
    [ADXL355-TO-ETHERNET.kicad_pcb, ADXL355-TO-ETHERNET.kicad_sch, ADXL_eth_con.brd, ADXL_eth_con.sch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]

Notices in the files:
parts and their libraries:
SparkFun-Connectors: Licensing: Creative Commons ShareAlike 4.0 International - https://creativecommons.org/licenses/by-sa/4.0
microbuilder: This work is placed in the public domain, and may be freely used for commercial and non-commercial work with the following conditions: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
